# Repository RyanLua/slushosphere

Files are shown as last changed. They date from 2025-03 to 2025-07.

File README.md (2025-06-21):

# Slushosphere

Slushosphere is a project to make slushies in the [stratosphere](https://en.wikipedia.org/wiki/Stratosphere) via high-altitude-balloons (HAB) and record the altitude in which water becomes a slushie. When water is exposed to low pressure, it boils at a lower temperature. At the same time, it freezes because of the cold temperatures in the stratosphere. We predict because of this, water will turn into a slush in the stratosphere.

How we will achieve this is using an Arduino with an environmental shield that has ambient temperature, humidity, and pressure sensors. A GPS shield will be used to record the location and altitude of the balloon along with time. A connector carrier to connect a submersible temperature sensor to measure the temperature of the water. A microSD card on the environmental shield to record all the data and a battery connected to the Arduino to power it all.

This project is a part of [Apex Hacks 2025](https://apex.hackclub.com) from [Hack Club](https://hackclub.com). Apex has provided us with the resources to make this project a reality including funding, travel and lodging, and a team of event organizers to help us along the way.

Apex wordmark (https://apex.hackclub.com)

## Code

You can use either [Arduino IDE 2](https://docs.arduino.cc/software/ide/#ide-v2) or [Visual Studio Code](https://code.visualstudio.com) with [arduino-cli](https://arduino.github.io/arduino-cli) to upload the code to the Arduino MKR WiFi 1010.

The code for the Arduino is separated into two variants, the one measuring using [a temperature sensor on the Arduino MKR ENV Shield](RecorderAmbient/RecorderAmbient.ino) and the one measuring using [a submersible temperature sensor connected to the Arduino MKR Connector Carrier](RecorderProbe/RecorderProbe.ino). The `RecorderAmbient` was used for our launch because we did not have the submersible temperature sensor at the time. Note that the `RecorderProbe` is outdated because of this and has never been tested.

### LED key

The MKR WiFi 1010's built-in RGB LED is used to indicate the status of the Arduino and its components. The LED will show the following colors:

- Blue: Initializing 
  - The Arduino is starting up and initializing the components.
- Red: Error
  - The Arduino has encountered an error and is unable to continue.
- Blinking Green: Fully working
  - The Arduino is fully operational and all components are functioning correctly.

When you turn on the device, the LED will be blue while it initializes and then turn off when it finishes. If there is a GPS signal, the LED will turn green and start blinking. If there is an error with any of the components, the LED will turn red.

Each time the LED flashes green, it means that it has successfully recorded a data point.

## Hardware

We are using the [Arduino Environmental Monitor Bundle](https://store-usa.arduino.cc/products/environmental-monitor-bundle) which includes the following parts:

- [Arduino MKR WiFi 1010](https://store-usa.arduino.cc/products/arduino-mkr-wifi-1010)
  - This is the main board that will run the code and connect to the shields and carriers.
- [Arduino MKR ENV Shield rev2](https://store-usa.arduino.cc/products/arduino-mkr-env-shield-rev2)
  - This shield has the sensors to measure ambient temperature, humidity, and pressure. It also has a microSD card slot to record the data.

In addition to the bundle, we are using the following parts:

- [Arduino MKR GPS Shield](https://store-usa.arduino.cc/products/arduino-mkr-gps-shield)
  - This shield has a GPS module to record the location and altitude of the balloon. It also has a real-time clock (RTC) which will be used to record the time of the data.
- [Arduino MKR Connector Carrier](https://store-usa.arduino.cc/collections/shields-carriers/products/arduino-mkr-connector-carrier-grove-compatible)
  - This carrier has Seeed Studio Grove connectors to connect our submersible temperature sensor from Seeed Studio.
- [One Wire Temperature Sensor DS18B20](https://www.seeedstudio.com/One-Wire-Temperature-Sensor-p-1235.html)
  - This is a submersible temperature sensor that will be used to measure the temperature of the water. It is connected to the MKR Connector Carrier.

### Collected data

The data collected by the Arduino MKR WiFi 1010 will be stored in a microSD card in the Arduino MKR ENV Shield. The data will be in CSV format with the following columns:

- `Timestamp (Epoch)`: The time the data was recorded in epoch format.
- `Temperature (°C)`: The ambient temperature in degrees Celsius measured by the MKR ENV Shield.
- `Humidity (%)`: The ambient humidity in percentage measured by the MKR ENV Shield.
- `Pressure (kPa)`: The ambient pressure in kilopascals measured by the MKR ENV Shield.
- `Illuminance (lx)`: The ambient illuminance in lux measured by the MKR ENV Shield.
- `Liquid Temperature (°C)`: The temperature of the water in degrees Celsius measured by the submersible temperature sensor.
- `Latitude`: The latitude of the balloon's location measured by the MKR GPS Shield.
- `Longitude`: The longitude of the balloon's location measured by the MKR GPS Shield.
- `Altitude (m)`: The altitude of the balloon's location in meters measured by the MKR GPS Shield.
- `Speed (km/h)`: The speed of the balloon in kilometers per hour measured by the MKR GPS Shield.
- `Satellites`: The number of satellites used to calculate the location and altitude measured by the MKR GPS Shield.

The data recorded is available in [`DATA.CSV`](data/DATA.CSV). You can process the data using the [`data.ipynb`](notebooks/data.ipynb) Jupyter notebook.

## Materials

We can see the [Bill of Materials](Bill%20of%20Materials.csv) we used to make this project. It will contain the manufacturer and Amazon links for you to buy the materials. The total cost of the materials is under 400 USD.

All materials have been checked to operate as low as -20°C. You can see the [Datasheet](Datasheet.md) for each electronic's official datasheet with operating temperatures.

### Student discounts

Discounts you can use if you are a student and doing this project.

- [Ardiuno offers 25% off the Ardiuno MKR Family and more](https://www.arduino.cc/education/github-students)
  - Helpful if you are only buying [Arduino MKR WiFi 1010](https://store.arduino.cc/products/arduino-mkr-wifi-1010). We are not using this because is cheaper to buy the [Arduino Environmental Monitor Bundle](https://store-usa.arduino.cc/products/environmental-monitor-bundle) rather than individually with the discount.
- [Adafruit offers discounts on certain Adafruit products](https://www.adafruit.com/github-students)
  - None of the discounts are for our parts so we cannot use it.
- [Amazon has Prime Student membership which is cheaper than Prime](https://www.amazon.com/joinstudent)
  - If you want faster and free delivery and exclusive Prime discounts. They were no exclusive Prime discounts for our materials at the time of the project.

## Notes

### Altitude tracking

If you're using a different GPS, make sure it works over 60,000 ft since most do not.

If you're using a barometer to get pressure and derive altitude from it, make sure records as low as 10 hPa or you may get inaccurate altitude. Most barometers don't measure that low.

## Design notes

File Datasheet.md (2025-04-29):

# Project Datasheet

Datasheet for weight of non-electronics used in the project.

| Item                                       | Weight (g) | Manufacturer Link                               |
| ------------------------------------------ | ---------- | ----------------------------------------------- |
| Polar Tech Thermo Chill 207/T16C 8 x 6 x 7 | 31         | https://www.polar-tech.com/shop/item/207%2Ft16c |

# Electronics Datasheet

Datasheet for the electronics used in the project. Some Fritzing links are not official and may not be up to date. If you find an official Fritzing link, please let us know so we can update it.

| Item                                              | Temperature range (°C) | Weight (g) | Datasheet Link                                                                                                          | Fritzing Link                                                                                              |
| ------------------------------------------------- | ---------------------- | ---------- | ----------------------------------------------------------------------------------------------------------------------- | ---------------------------------------------------------------------------------------------------------- |
| Arduino MKR WiFi 1010                             | -20 to +80             | 32         | https://docs.arduino.cc/resources/datasheets/ABX00023-datasheet.pdf                                                     | https://content.arduino.cc/assets/Arduino%20MKR%20WIFI%201010.fzpz                                         |
| Arduino MKR ENV Shield rev2                       | -40 to +120            | 32         | https://www.st.com/resource/en/datasheet/hts221.pdf                                                                     | https://content.arduino.cc/assets/Arduino%20MKR%20ENV%20Shield.fzpz                                        |
| Arduino MKR GPS Shield                            | -40 to +85             | 14         | https://content.arduino.cc/assets/Arduino-MKR-GPS-Shield_u-blox8-SAM-M8Q_DataSheet_UBX-16012619.pdf                     | https://forum.fritzing.org/uploads/short-url/vtJmwPP0qo7ksIrhe34RObGyFl4.fzpz                              |
| Arduino MKR Connector Carrier                     |                        | 32         | https://store-usa.arduino.cc/collections/shields-carriers/products/arduino-mkr-connector-carrier-grove-compatible       | https://forum.fritzing.org/uploads/short-url/aA5wYZ3b2lv6sQEg6W6jkxjTFgw.fzpz                              |
| Adafruit Lithium Ion Polymer Battery 3.7v 1200mAh | -20 to +60[^1]         | 23         | https://cdn-shop.adafruit.com/product-files/258/C101-_Li-Polymer_503562_1200mAh_3.7V_with_PCM_APPROVED_8.18.pdf         | https://github.com/adafruit/Fritzing-Library/raw/refs/heads/master/parts/LiPoly%20Battery%20(1300mAh).fzpz |
| One Wire Temperature Sensor DS18B20               | -10 to +85[^2]         | 54         | https://files.seeedstudio.com/wiki/One-Wire-Temperature/res/DS18B20-Datasheet.pdf                                       | https://forum.fritzing.org/uploads/short-url/1y9gVcpzoVgtYc0VBdMwWpETT2A.fzpz                              |
| SanDisk MAX ENDURANCE microSD Card 32GB           | -40 to +85             | 5          | https://shop.sandisk.com/products/memory-cards/microsd-cards/sandisk-max-endurance-uhs-i-microsd?sku=SDSQQVR-032G-GN6IA |                                                                                                            |

[^1]: Discharge temperature range. Does not include charging temperature range.
[^2]: We only measure when it freezes (0°C), so it's fine it can't measure as low as -20°C.

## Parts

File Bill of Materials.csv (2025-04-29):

Item | Description | SKU | Manufacturer Link | Amazon Link
Arduino Environmental Monitor Bundle | Data storage and temperature measurement | VB00012 | https://store-usa.arduino.cc/products/environmental-monitor-bundle | https://www.amazon.com/dp/B0B39S11K1
Arduino MKR Connector Carrier | Connect board with One Wire Temperature Sensor | ASX00007 | https://store-usa.arduino.cc/collections/shields-carriers/products/arduino-mkr-connector-carrier-grove-compatible | https://www.amazon.com/dp/B07JKVW8XT
Arduino MKR GPS Shield | GPS module for location tracking | ASX00017 | https://store-usa.arduino.cc/products/arduino-mkr-gps-shield | https://www.amazon.com/dp/B084DT7ZLQ
Adafruit Lithium Ion Polymer Battery 3.7v 1200mAh | Battery to power the board | 258 | https://www.adafruit.com/product/258 | https://www.amazon.com/dp/B00J2QET64
Adafruit Micro-Lipo Charger for LiPo/LiIon Batt w/MicroUSB Jack - v1 | Charger for the battery | 1904 | https://www.adafruit.com/product/1904 | https://www.amazon.com/dp/B00SK8J94M
One Wire Temperature Sensor DS18B20 | Measure liquid freezing | 101990019 | https://www.seeedstudio.com/One-Wire-Temperature-Sensor-p-1235.html
SanDisk MAX ENDURANCE microSD Card 32GB | Data storage | SDSQQVR-032G-GN6IA | https://shop.sandisk.com/products/memory-cards/microsd-cards/sandisk-max-endurance-uhs-i-microsd?sku=SDSQQVR-032G-GN6IA | https://www.amazon.com/dp/B084CJLNM4
Polar Tech Thermo Chill 207/T16C 8 x 6 x 7 | Box to hold project | 207/T16C | https://www.polar-tech.com/shop/item/207%2Ft16c | https://www.amazon.com/dp/B007ICA67U

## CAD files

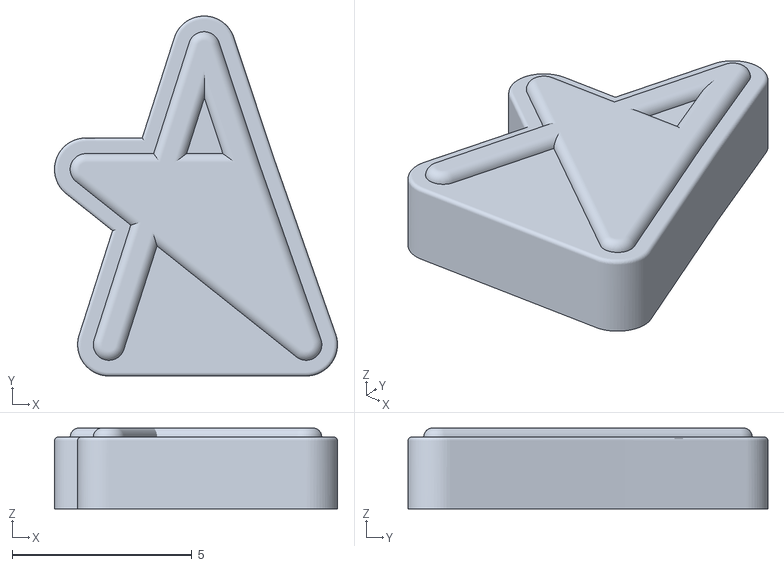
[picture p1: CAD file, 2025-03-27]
Apex Popsicle.stl
7.86 x 10.0 x 2.25

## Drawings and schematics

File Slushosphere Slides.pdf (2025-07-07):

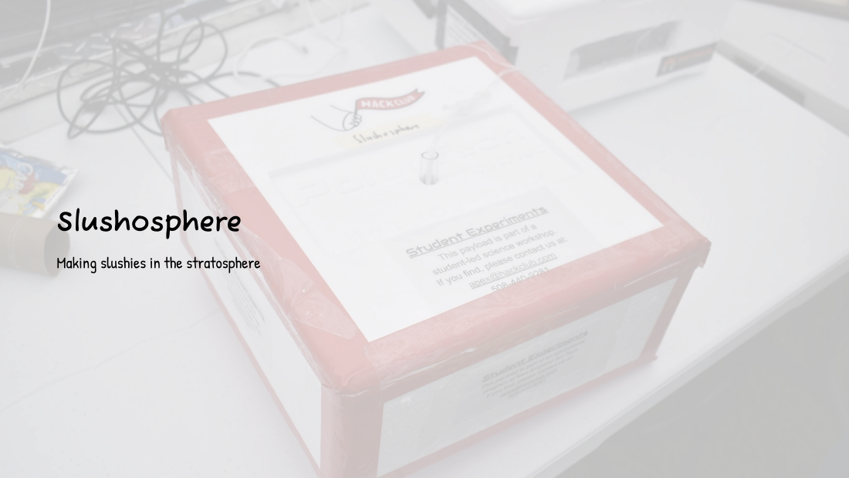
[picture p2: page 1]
Slushosphere

Making slushies in the stratosphere

# Project Code

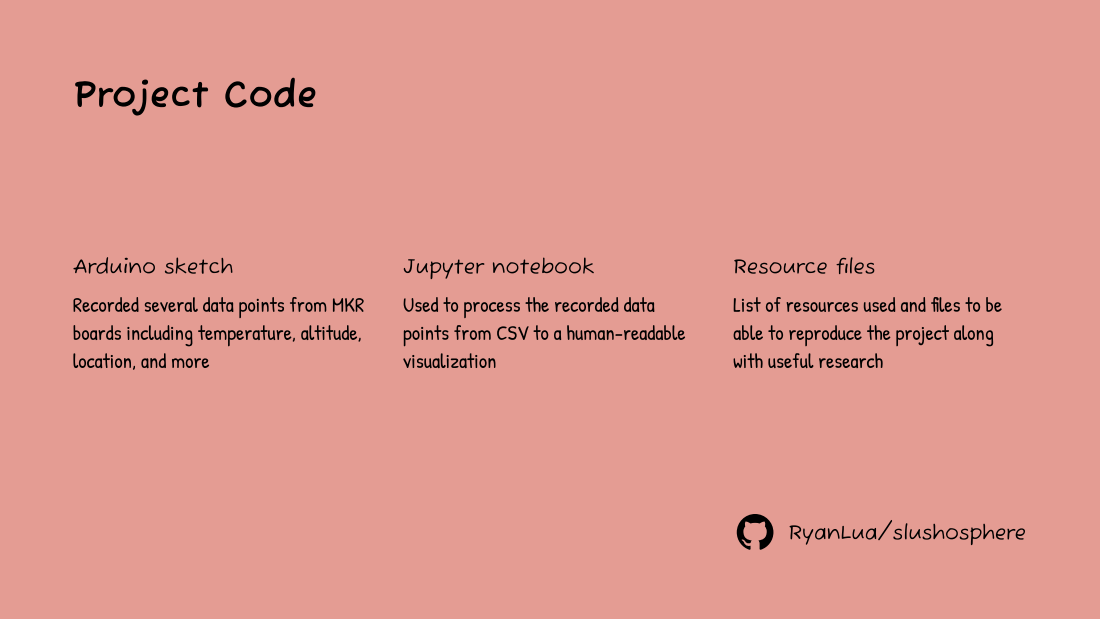
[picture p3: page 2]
RyanLua/slushosphere; Arduino sketch; Jupyter notebook; visualization; Resource files

Recorded several data points from MKR

Used to process the recorded data

List of resources used and files to be

boards including temperature, altitude,

points from CSV to a human-readable

able to reproduce the project along

location, and more

with useful research

# Materials List

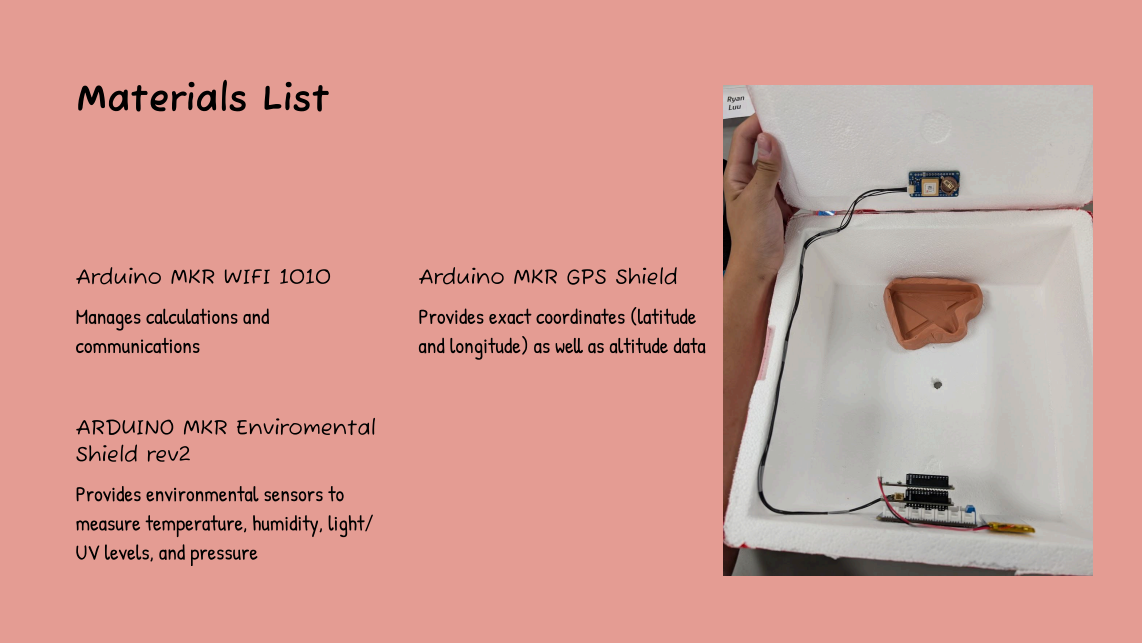
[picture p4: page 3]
communications

Arduino MKR WIFI 1010

Arduino MKR GPS Shield

Manages calculations and

Provides exact coordinates (latitude

and longitude) as well as altitude data

ARDUINO MKR Enviromental
Shield rev2

Provides environmental sensors to

measure temperature, humidity, light/

UV levels, and pressure

# Contributors

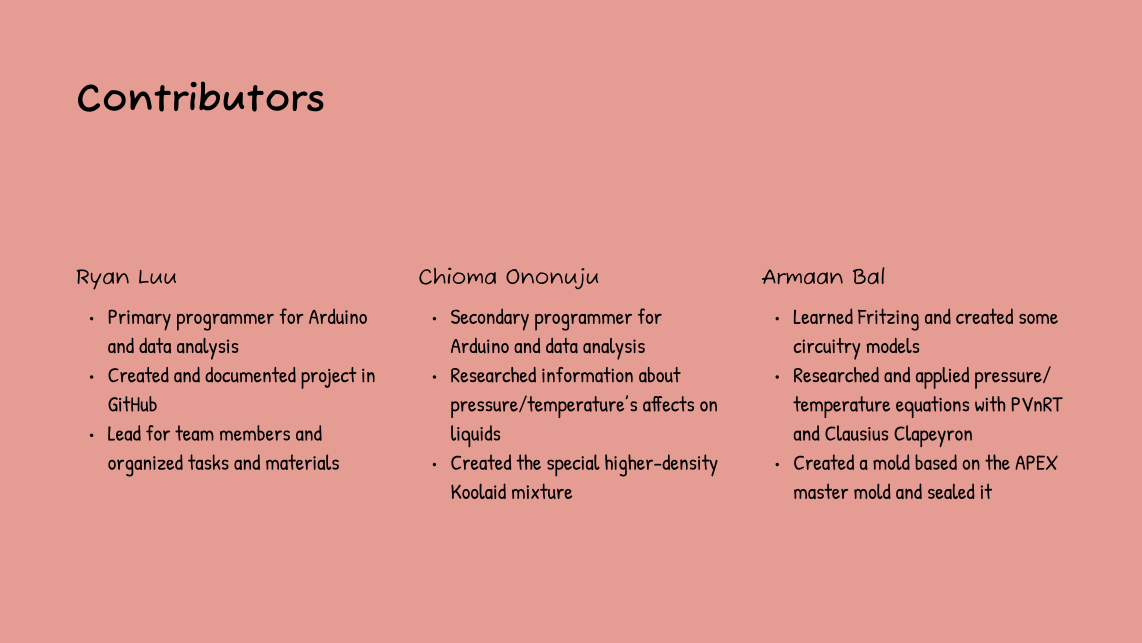
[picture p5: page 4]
Ryan Luu; GitHu; Chioma Ononuju; Koolaid mixture; Armaan Bal; circuitry models}

- Primary programmer for Arduino

- Secondary programmer for

- Learned Fritzing and created some

and data analysi

Arduino and data analysi

- Created and documented project in

- Researched information about

- Researched and applied pressure/

pressure/temperature’s affects on
liquid

temperature equations with PVnRT

- Lead for team members and

and Clausius Clapeyroz

organized tasks and materials

- Created the special higher-density

- Created a mold based on the APEX

master mold and sealed it

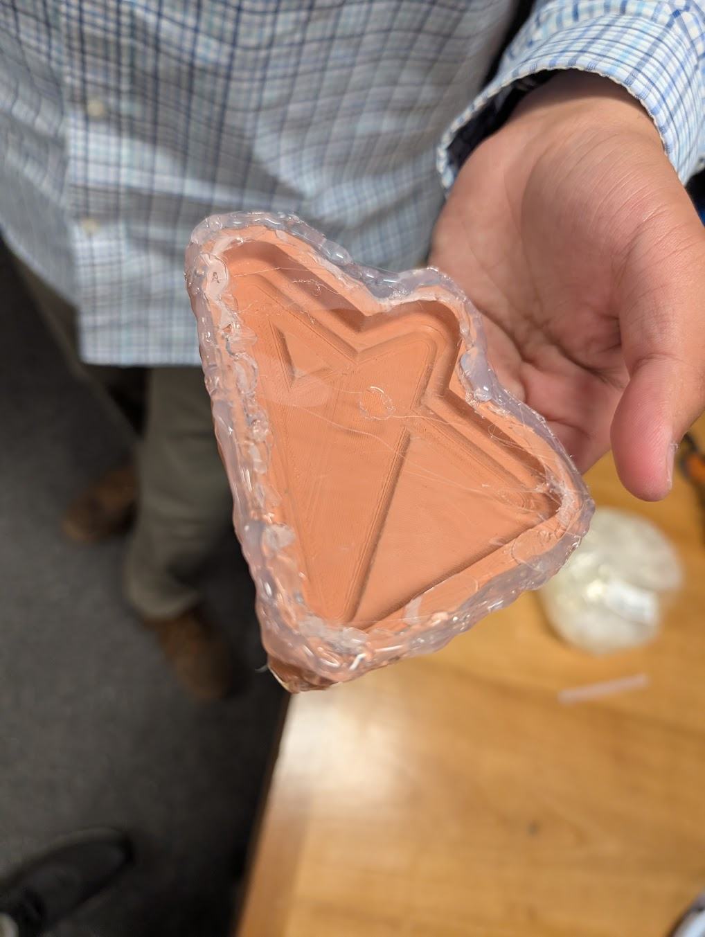
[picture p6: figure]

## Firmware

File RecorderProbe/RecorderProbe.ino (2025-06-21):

/*
  Record data from sensors into microSD card
*/

#include <Arduino_MKRENV.h>
#include <Arduino_MKRGPS.h>
#include <SPI.h>
#include <SD.h>
#include <OneWire.h>
#include <string>
#include <DallasTemperature.h>
#include <WiFiNINA.h>
#include <utility/wifi_drv.h>

// TODO: Change this when we have a physical prototype
// Data wire is plugged into port 2 on the Arduino
#define ONE_WIRE_BUS 2

OneWire oneWire(ONE_WIRE_BUS);
DallasTemperature sensors(&oneWire);
String filename = "data.csv";

void setup() {
  WiFiDrv::pinMode(25, OUTPUT);  //define GREEN LED
  WiFiDrv::pinMode(26, OUTPUT);  //define RED LED
  WiFiDrv::pinMode(27, OUTPUT);  //define BLUE LED

  setLED(LOW, LOW, HIGH);  // BLUE

  Serial.begin(9600);

  // MKR ENV shield
  if (!ENV.begin()) {
    Serial.println("MKR ENV shield failed to initialize!");
    setLED(HIGH, LOW, LOW);  // RED
    while (1)
      ;
  }

  // MKR GPS Shield
  if (!GPS.begin()) {
    Serial.println("MKR GPS Shield failed to initialize!");
    setLED(HIGH, LOW, LOW);  // RED
    while (1)
      ;
  }

  // microSD Card
  if (!SD.begin(4)) {
    Serial.println("microSD card failed to initialize!");
    setLED(HIGH, LOW, LOW);  // RED
    while (1)
      ;
  }

  // One Wire Temperature Sensor
  sensors.begin();

  Serial.println("Successfully initialized sensors.");

  // Open data file
  // File dataFile = SD.open(filename, FILE_WRITE);
  File dataFile = SD.open(filename);

  // Write data file if missing
  if (dataFile) {
    Serial.println("Data file already exists, appending data.");
    dataFile.close();
  } else if (!SD.exists(filename)) {
    Serial.println("Writing new data file...");
    dataFile = SD.open(filename, FILE_WRITE);
    dataFile.println("Timestamp (Epoch),Temperature (°C),Humidity (%),Pressure (kPa),Illuminance (lx),Liquid Temperature (°C),Latitude,Longitude,Altitude (m),Speed (km/h),Satellites");
    dataFile.close();
  } else {
    Serial.println("Unknown error checking data file!");
    setLED(HIGH, LOW, LOW);  // RED
  }

  Serial.println("Successfully initialized SD card.");
}

void loop() {
  if (GPS.available()) {
    setLED(LOW, HIGH, LOW);  // GREEN

    // Fetch data from sensors
    sensors.requestTemperatures();

    float temperature = ENV.readTemperature();  // MKR ENV Shield
    float humidity = ENV.readHumidity();
    float pressure = ENV.readPressure();
    float illuminance = ENV.readIlluminance();
    float latitude = GPS.latitude();  // MKR GPS Shield
    float longitude = GPS.longitude();
    float altitude = GPS.altitude();
    float speed = GPS.speed();
    int satellites = GPS.satellites();
    unsigned long epochTime = GPS.getTime();
    float liquidTemperature = sensors.getTempCByIndex(0);  // One Wire Temperature Sensor

    if (liquidTemperature == DEVICE_DISCONNECTED_C) {
      Serial.println("Liquid temperature sensor disconnected!");
      setLED(HIGH, LOW, LOW);  // RED
    }

    // Print sensor data to serial
    Serial.print("Epoch time: ");
    Serial.println(epochTime);

    Serial.print("Temperature = ");  // MKR ENV Shield
    Serial.print(temperature);
    Serial.println(" °C");

    Serial.print("Humidity = ");
    Serial.print(humidity);
    Serial.println(" %");

    Serial.print("Pressure = ");
    Serial.print(pressure);
    Serial.println(" kPa");

    Serial.print("Illuminance = ");
    Serial.print(illuminance);
    Serial.println(" lx");

    Serial.print("Liquid Temperature = ");
    Serial.println(liquidTemperature);
    Serial.print(" °C");

    Serial.print("Location = ");  // MKR GPS Shield
    Serial.print(latitude, 7);
    Serial.print(", ");
    Serial.println(longitude, 7);

    Serial.print("Altitude = ");
    Serial.print(altitude);
    Serial.println("m");

    Serial.print("Ground speed = ");
    Serial.print(speed);
    Serial.println(" km/h");

    Serial.print("Number of satellites = ");
    Serial.println(satellites);

    Serial.println();  // Print empty line

    // Write sensor data to data file
    File dataFile = SD.open(filename, FILE_WRITE);

    if (dataFile) {
      // TODO: See what happens when the sensor is disconnected and we try to write the data
      String dataString = String(epochTime) + ",";
      dataString += String(temperature) + ",";
      dataString += String(humidity) + ",";
      dataString += String(pressure) + ",";
      dataString += String(illuminance) + ",";
      dataString += String(liquidTemperature) + ",";
      dataString += String(latitude, 7) + ",";
      dataString += String(longitude, 7) + ",";
      dataString += String(altitude) + ",";
      dataString += String(speed) + ",";
      dataString += String(satellites);

      dataFile.println(dataString);
      dataFile.close();
    } else {
      Serial.println("Error writing to data file!");
      setLED(HIGH, LOW, LOW);  // RED
    }
  } else {
    setLED(LOW, LOW, LOW);  // NONE
  }
}

void setLED(PinStatus red, PinStatus green, PinStatus blue) {
  WiFiDrv::digitalWrite(25, red);
  WiFiDrv::analogWrite(26, green);  // Green should be dim to reduce power
  WiFiDrv::digitalWrite(27, blue);
}

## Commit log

2025-03-14 Add fritzing file
    [Pop Rockets.fzz]
2025-03-27 Add 3D print for popsicle
    [apex-popsicle.stl]
2025-03-27 Rename apex-popsicle.stl to Apex Popsicle.stl
    [Apex Popsicle.stl]
2025-04-03 Create Bill of Materials.csv
    [Bill of Materials.csv]
2025-04-03 Fix URL and names
    [Bill of Materials.csv]
2025-04-03 Add descriptions
    [Bill of Materials.csv]
2025-04-03 Shorten description
    [Bill of Materials.csv]
2025-04-03 Shorten name
    [Bill of Materials.csv]
2025-04-03 Add SKUs and ASINs
    [Bill of Materials.csv]
2025-04-03 Use long Amazon links
    [Bill of Materials.csv]
2025-04-03 Add microSD Card
    [Bill of Materials.csv]
2025-04-07 Add Amazon and Manufacturer link
    [Bill of Materials.csv]
2025-04-07 Fix CSV formatting
    [Bill of Materials.csv]
2025-04-07 Add basic README
    [Bill of Materials.csv]
2025-04-08 Add styrofoam box
    [Bill of Materials.csv]
2025-04-09 Change charger type
    [Bill of Materials.csv]
2025-04-09 Fix formatting
    [Bill of Materials.csv]
2025-04-09 Only show SKU
    [Bill of Materials.csv]
2025-04-09 Weigh enclosure
2025-04-24 Add GPS to list of materials
    [Bill of Materials.csv]
2025-04-24 Add error print
2025-04-29 Remove popsicle ingredients
    [Bill of Materials.csv]
2025-05-14 Fix println instead of print
2025-06-20 Add LED key
2025-06-21 Add LED diagnostics
2025-06-21 Add GPS LED
2025-06-21 Add new LED logic
2025-06-21 Improve LED docs
2025-06-21 Add notebooks
    [DATA.CSV]
2025-06-21 Update and rename DATA.CSV to MOCK_DATA.CSV
    [MOCK_DATA.CSV]
